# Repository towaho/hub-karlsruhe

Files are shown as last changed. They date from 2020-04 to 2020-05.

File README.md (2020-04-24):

# Herstellung der Gestelle - vom Druck bis zur Anlieferung
Vielen Dank, dass ihr uns mit dem Druck von Gestellen unterstützen wollt. Ihr findet hier alle wichtigen Informationen zum Ablauf im Hub Karlsruhe.
Alle weiteren Informationen zur Orga sowie ein FAQ findet ihr in unserem Doc [Organisation HUB Karlsruhe](https://docs.google.com/spreadsheets/d/1wsZU-VTYREOStcnClETrNQFkIYqHXFwlxU8IcKh8BXk)

Die Koordinierung für den Großraum Karlsruhe erfolg im Kanal [#hub-karlsruhe](https://app.slack.com/client/T010HM3B6BS/C010VSH5RD5). Dort helfen wir euch gerne bei Fragen und Problemen und ihr bekommt Infos zum aktuellen Stand.

In Karlsruhe wird aktuell ausschließlich das Modell Prusa rc3 bzw. die dazu lochkompatiblen Versionen V10 und V18 gedruckt.
Dieses Modell wird am meisten gewünscht und ist vor allem mit anderen Hubs kompatibel. Wir möchten euch daher bitten, nur dieses zu drucken und anzuliefern. Achtet bitte darauf, dass ihr **NICHT** aus versehen die slim Variante druckt. Die STL-Dateien sowie Hinweise zum Drucken findet ihr weiter unten.

Der Zusammenbau erfolgt in den beiden FabLabs. Ihr müsst also keine fertigen Schilde anliefern, sondern nur die gedruckten Gestelle und Stabis. Falls ihr passende Folien oder Loch-Gummiband beschaffen könnt, meldet euch aber gerne im slack Kanal bei uns oder direkt beim [Orga-Team](https://docs.google.com/spreadsheets/d/1wsZU-VTYREOStcnClETrNQFkIYqHXFwlxU8IcKh8BXk/edit#gid=139873882) per direct message.

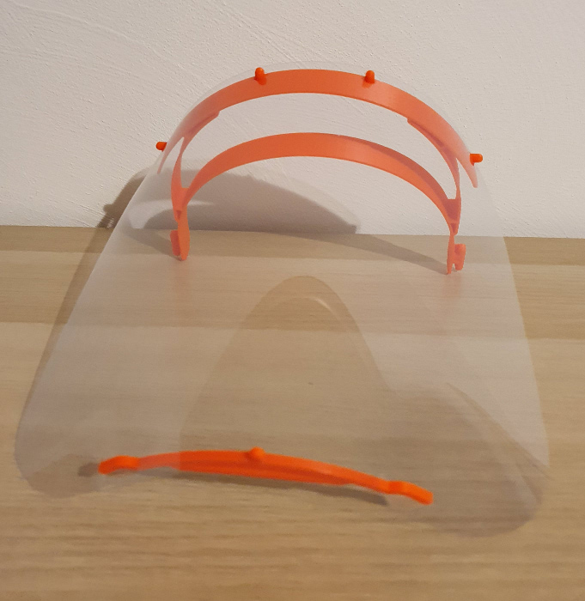
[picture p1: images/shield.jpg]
Faceshield


## Eintrag als Drucker
Tragt euch bitte im [doc in der Tabelle "Kapazitäten Gestelle"](https://docs.google.com/spreadsheets/d/1wsZU-VTYREOStcnClETrNQFkIYqHXFwlxU8IcKh8BXk/edit#gid=0) ein und gebt bitte eure Slack ID mit an. An eure Slack-ID kommt ihr wie folgt:
* In Slack in deinem Fenster oben Links auf das Feld "MakerVSVirus" klicken
* auf Profil Anzeigen / View Profile klicken
* Der Link wird dann im Browser in der URL-Leiste angezeigt

Die beiden geliefert Spalten sind schreibgeschützt und werden von den beiden Hubs verwaltet.

Spalte | Hinweise
------------ | -------------
Anzahl gedruckt | Hier bitte die Summe aller bereits gedruckten Gestelle eintragen (inklusive der bereits ans HUB gelieferten)
Anzahl in Arbeit | Hier könnt ihr eintragen, wie viele Gestelle ihr zur Zeit gleichzeitig im Druck habt. Wenn ihr gerade nicht drucken könnt, bitte auf 0 ändern.
mögliche Anzahl pro 24h | Tragt hier bitte nur ganze Zahlen ein und nicht "5-10" oder ähnliches.

## Material
PETG sowie PLA gehen. Bevorzugt wird PETG, da besser reinigbar. Die Farbe ist grundsätzlich egal. Sie sollte natürlich nicht ganz so peinlich sein. 

## STL Dateien
### Gestell
Unsere Empfehlung: [Covid-19 Shield v18.stl von Yannic Schröder](https://github.com/yschroeder/face-shield/raw/master/stl/Covid-19%20Shield%20v18.stl)

Wenn ihr Probleme mit der Haftung auf dem Druckbett habt, könnt ihr auch die [Version mit Lily Pads](https://github.com/yschroeder/face-shield/raw/master/stl/Covid-19%20Shield%20v18%20Lily.stl) nutzen. Das erhöht jedoch den Aufwand bei der Nachbearbeitung. Bei einem Drucker mit beheiztem Druckbett, richtig eingestellter Temperatur und korrekt justierter Z-Achse, solltet ihr aber auch ohne Pads keine Haftungsprobleme bekommen.

Für den Prusa i3 mit der Standard 0.4er nozzle findet ihr [hier eine fertige Projektdatei](https://github.com/towaho/hub-karlsruhe/raw/master/stl/Covid-19_Shield_v18_twin.3mf) mit zwei Oberteilen. Der [PrusaSlicer 2.2](https://www.prusa3d.de/prusaslicer/) unterstützt auch out of the box den Ender 3.

#### Alternativen (Bitte NICHT die slim Variante drucken)
* [Prusa rc3 ohne Text](https://media.prusaprinters.org/media/prints/25857/stls/270587_b59f75d0-4b8a-4999-8417-e5e75874ff98/covid19_headband_rc3.stl)
* [Covid-19 Shield v10](https://github.com/yschroeder/face-shield/raw/master/stl/Covid-19%20Shield%20v10.stl)

Es gibt zwar von Prusa auch eine Vorlage für kleinere Druckbette, diese müssen aber zusammen geklebt werden. Wir haben jedoch das Feedback erhalten, dass bei diesen der Tragekomfort nicht so gut ist. Daher diese Version bitte nicht mehr drucken.

### Stabi ("Unterteil")
Das Unterteil bitte nicht mehr drucken. Zur Zeit liefern wir alle Schilde ohne aus, da die Folie dick genug ist.

## Druck
Mit den Standardeinstellungen beträgt die Druckdauer eines Gestells in PETG ca. 2:30h. Die V18 ist von Yannic für den schnellen Druck optimiert worden. Bevor ihr diese nutzt, lest euch bitte vorher die [Doku von Yannic](https://github.com/yschroeder/face-shield) durch und stellt eueren Drucker entsprechend ein. Eine [deutsche Übersetzung](https://github.com/crix26/face-shield/blob/master/README.md) erstellt aktuell Christoph C. Mit Yannics Einstellungen könnt ihr ein Oberteil mit einem prusa i3 in PETG in ca. **0:43h** drucken. Zwei Gestelle gleichzeitig in 1:27h.

Beachtet bitte auch die Hinweise unter "Advanced Parameter Tuning" sowie Holes:

**Extrusion width / Extrusionsbreite**
* External perimeters / Außenkontouren: 1.00mm
* solid infill / Massives Infill: 0.55mm
* top solid infill / oberes massives Infill: 0.55mm

Hier zum Vergleich eine Detailaufnahme mit 0.87mm. Es sind an den T-Kreuzungen deutlich kleinere Löcher zu erkennen:
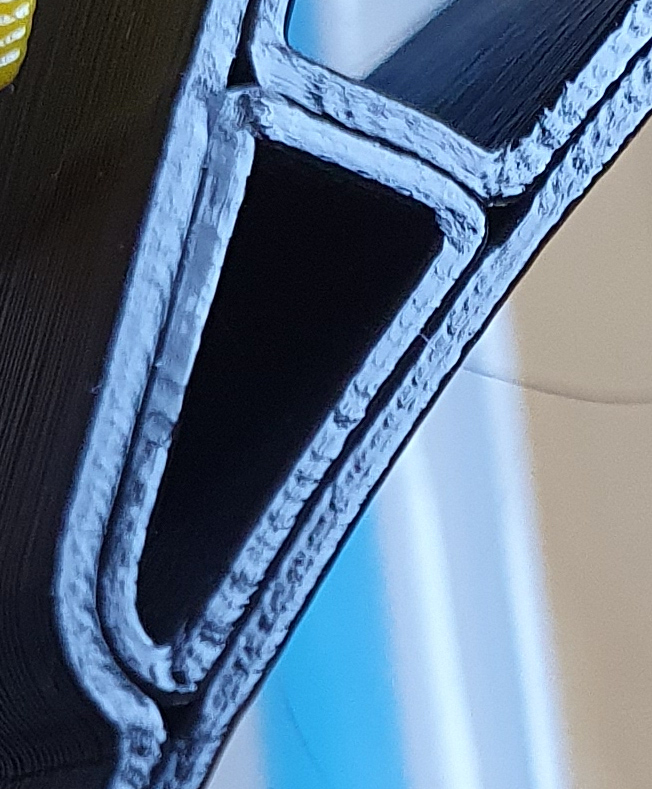
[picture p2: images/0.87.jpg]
0.87mm external perimeters


Mit 1.00mm sind zwar noch kleine Rillen vorhanden, aber die Löcher sind zu:
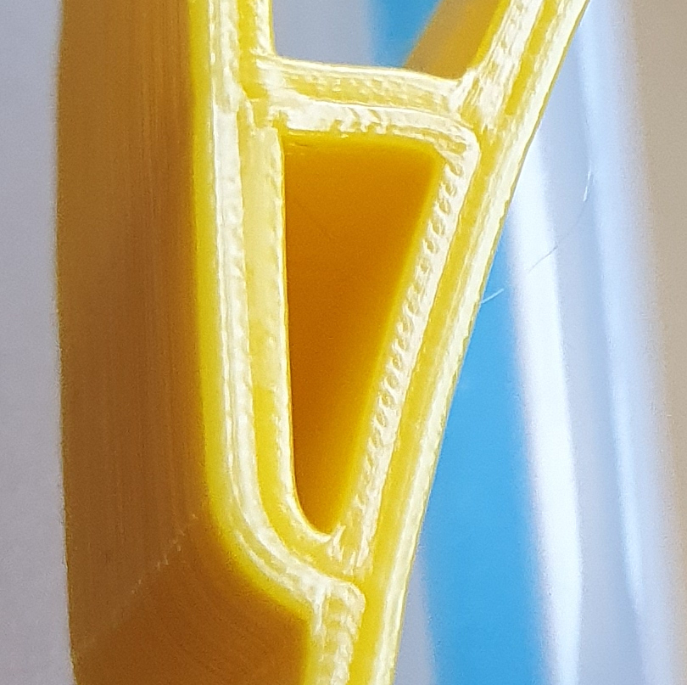
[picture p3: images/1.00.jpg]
1.00mm external perimeters


Alternativ könnt ihr auch wie von Yannic beschrieben den "Extrusion multiplier" erhöhen.

Wenn ihr die oben verlinkte Projektdatei nutzt, sind die hier beschriebenen Einstellungen schon alle mit drin. Um die angebenenen Druckzeiten zu erreichen, müsst ihr aber auch noch wie von Yannic beschrieben die Werte für "Max volumetric speed" unter "Filament Settings" -> Advanced -> "Print speed override" anpassen. Ein guter Startwert ist 8 mm³/s. Der i3 schafft mit 0.4er nozzle aber im Normalfall auch 17mm³/s. Am besten erhöht ihr wie von Yannic beschrieben den Wert in 2er Schritten, bis ihr einen optimalen Wert für euren Drucker gefunden habt.

### Hinweise

Das Drucken der Gestelle ist kein Wettbewerb wer am meisten druckt. Wenn ihr nicht die von Yannic empfohlenen Einstellungen nutzt, dann am besten mit 3 Perimeter (Wände) drucken. Vor dem ersten Druck sollte auch in der Vorschau überprüft werden, ob keine Lücken entstehen.

Aktuell raten wir davon ab, die Gestelle übereinander als Stacks zu drucken. Die bisherigen Erfahrungen haben gezeigt, dass gut 80% der Stacks nicht verwendbar sind (kleben zu stark aneinander, Boden schlecht verklebt, Probleme beim Desinfizieren).

### Empfehlungen für das BASF PET Fillament
Beachtet bitte, dass es sich hierbei um PET und nicht um PETG handelt. Der Schmelzpunkt ist niedriger und somit auch die Drucktemperatur. Wenn ihr ein PEI beschichtes Druckbett nutzt, dann solltet ihr beim ersten Druck die z-Achse 0.1mm höher (weiter Weg vom Druckbett) einstellen und euch in 0.01er Schritten an 0 annähern. ZU NAH AM BETT = RISIKO dass die Beschichtung beim Ablösen am Druckteil statt am Druckbett klebt! Löst die Teile am besten, bevor das Druckbett vollständig abgekühlt ist. 

Als Ausgangswerte für eigene Tests eignen sich:
* Druckbett 75°C (wenn die Haftung zu stark ist, senkt die Temperatur ein wenig)
* Nozzle: 220°C 
* Lüfter: 100%, durchgängig an, bis auf die ersten 1-2 Schichten
* Geschwindigkeit: max 60mm/s
* retraction Speed: 45mm/s vermindert das stringing nochmal ein wenig. Wenn ihr unsicher seid, lasst die default Einstellungen

Ein wenig stringing hatten wir auch mit diesen Einstellungen noch. Meldet euch gerne im channel, wenn ihr Probleme oder bessere Einstellungen gefunden habt.

Wer cura nutzt, findet hier auf der [Herstellerseite](https://www.ultrafusefff.com/3dprintingprofiles/) Profile für das Filament. Diese haben wir aber aktuell noch nicht getestet.

## Qualitätskontrolle
**Die hier beschriebenen Tests gelten nur für die V18**. Die anderen Modelle sind nicht so flexibel und könnten brechen obwohl sie für den Bau der Schilde nutzbar sind.

Viel wichtiger als die Druckzeit ist, dass die Qualität am Schluss stimmt. Prüft bitte insbesondere beim Druck der V18 mit nur zwei Perimeter, ob diese sauber miteinander kleben. 

So sollte es **nicht** aussehen (Delamination)
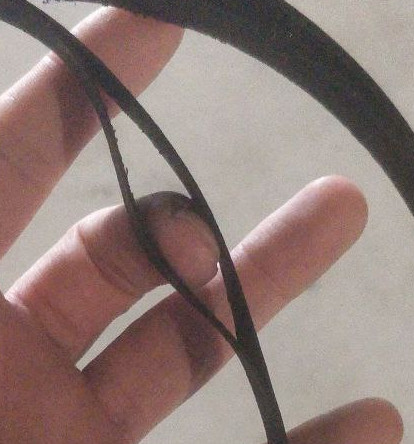
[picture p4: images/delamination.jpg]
Delamination


Führt am besten nach eurem ersten Druck den [hier beschriebenen Test](https://github.com/yschroeder/face-shield/blob/master/quality_control.md) durch. Meldet euch bitte im #hub-karlsruhe wenn ihr Qualitätsprobleme habt. **Vor der Abgabe/Abholung bitte alle Teile entsprechend prüfen.**

## Abgabe/Abholung
Abgeben könnt die fertig gedruckten Teile in einem der beiden FabLabs:

**FabLab Karlsruhe e.V.**
```
Alter Schlachthof 13a (gegenüber Substage / Alte Hackerei)
76131 Karlsruhe
Tel.:  +49 721 60906012	
```

**FabLab Bruchsal e.V. i.G.**
```
Werner-von-Siemens-Straße 2-6
Gebäude 5137c
76646 Bruchsal
Tel.: +49 151 25351131
```

Im Google Docs gibt es eine Ampel, ob das Lab besetzt ist. Fragt bitte vorher zur Sicherheit noch einmal telefonisch nach, damit ihr euch nicht umsonst auf den Weg macht.

Für alle die keine Möglichkeit haben, die Teile in Karlsruhe oder Bruchsal abzugeben, gibt auch ca. 2 mal die Woche eine Abholtour, bei der ihr eure Teile kontaktlos abholen lassen könnt. 

Damit wir euch bei Problemen direkt ansprechen können, bitte die Gestelle in einem Müllbeutel verpacken und einen Zettel mit folgenden Infos dazu legen:
* Name
* Slack ID
* Material
* Druckdatum/Zeitraum

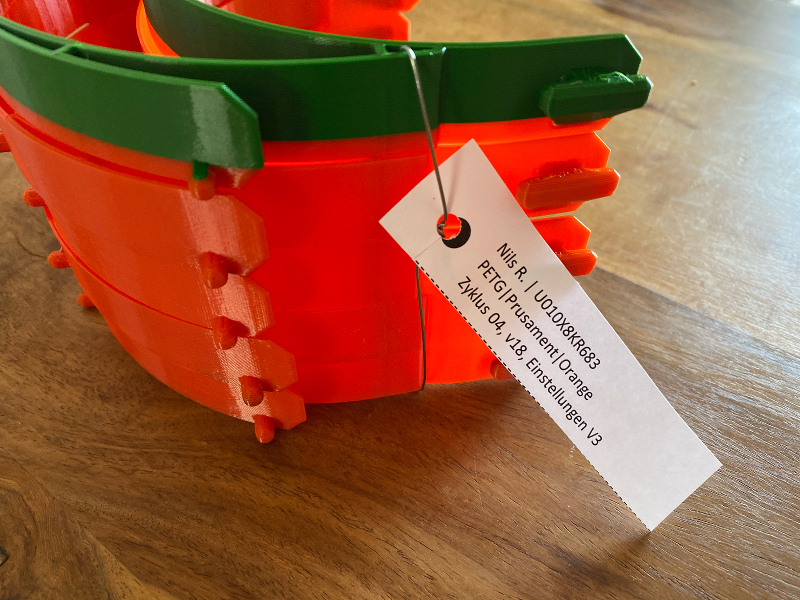
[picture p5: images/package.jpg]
Fertig zur Abgabe


Das Desinfizieren der Teile ist nicht notwendig. Die Empfänger werden die Schilde sowieso desinfizieren und Desinfektionsmittel ist zur Zeit ebenfalls knapp.

Falls wir die gelieferten Teile nicht im Sheet eingetragen haben, meldet euch bitte noch einmal bei uns.

[shield]: images/shield.jpg "Faceshield"
[1mmperimeters]: images/1.00.jpg "1.00mm external perimeters"
[0.87mmperimeters]: images/0.87.jpg "0.87mm external perimeters"
[delamination]: images/delamination.jpg "Delamination"
[package]: images/package.jpg "Fertig zur Abgabe"

## **Auslieferung**

Vielen Dank, dass du dich bereit erklärt hast auch fertig verpackte Gestelle auszuliefern.

Im folgenden sind einige Dinge beschrieben, die es zu beachten gibt, sowie FAQ.

### Auftragsbearbeitung/Zugriff auf die Tabelle

Die Auftragsbearbeitung wird über ein extra Google Sheet organisiert. Dies hat den Grund, dass die Kundendaten nicht für alle öffentlich einsehbar sein sollen. Kommt ein Auftrag über das Formular auf der Website rein, landet dies automatisch im Reiter "Kunden Daten". In den Reitern "[Labstandort]-Schilde offen" und "[Labstandort]-Masken offen] seht ihr welche Aufträge noch offen sind und entsprechend bearbeitet werden müssen/sollen.

Wichtig ist der Status der Bestellung. Steht dieser auf "In Herstellung" kann man sich den Auftrag zur Auslieferung reservieren. Mehr dazu in Ablauf Auslieferung.

Zugriff auf die Tabelle erhaltet ihr von einem der Admins. Das sind derzeit Robert & Nils R. .

Vor allem Robert schreibt des Öfteren Nachrichten zum Koordinieren, welche Lieferungen für den jeweiligen Tag anstehen. Diese sollten priorisiert abgearbeitet werden.

### Ablauf Auslieferung

1. Zugriff auf die Tabelle (siehe oben)
2. Auftrag von Robert (oder Nils) annehmen oder initiativ Auftrag annehmen (eher zu empfehlen wenn man schon einige Aufträge ausgeliefert hat und die Abläufe und Priorisierungen kennt)
3. In die Tabelle bei "Auslieferung durch" eintragen [Wichtig: Immer im Reiter "Kundendaten" Eintragungen vornehmen]
4. Klären, wann du die Lieferung im Lab abholen kannst. Im Reiter Kundendaten steht in der Spalte "sammeln in" wo du die Lieferung holen kannst.
5. Beim Kunden anrufen und Bescheid geben, dass und wann du vorhast auszuliefern. Eventuell Termin ausmachen, wenn nicht am selben Tag möglich.
6. Status von "In Herstellung" auf "In Auslieferung" ändern
7. Ausliefern (dabei erwähnen, dass wir uns immer über Bilder der Masken "Im Einsatz" zur Veröffentlichung auf unserer Website freuen) 
8. Status von "In Auslieferung" auf "Erledigt" ändern, Datum bei "Erledigt am" eintragen, Summe bei "[Art der Lieferung]-Erledigt-[Labstandort]" eintragen

Herzlichen Glückwunsch. Du hast erfolgreich deine erste Auslieferung durchgeführt! 

### FAQ oder was du noch wissen solltest: [bzgl. Auslieferung]

**Wie gehe ich mit Spenden um?**

Am Besten ist es, du verweist den Kunden auf das Spendenformular auf der Website. In der Regel stehen die Informationen dazu auch auf dem Zettel, welcher der Verpackung beigelegt ist.

Manche Einrichtungen oder Arztpraxen drücken einem auch manchmal einfach einen Umschlag in die Hand. Dieser sollte dann im Lab abgegeben werden. [Wichtig. Wenn der Kunde eine Spendenquittung wünscht, muss die Spende über das Spendenformular stattfinden!]

**Was soll ich sagen, wenn nach dem Preis gefragt wird?**

Grundsätzlich lautet die Antwort, dass die Schilde von uns kostenlos geliefert werden. Allerdings ist es schlau, immer darauf zu verweisen, dass wir ein Spendenformular haben und uns immer über Spenden freuen, da das Ganze nur so finanziert wird. [Wichtig: Die Spende ist freiwillig und so muss das auch kommuniziert werden. Es gibt auch Einrichtungen, denen schlichtweg das Geld fehlt und genau dafür gibt es uns ja]

**Was soll ich am Telefon sagen?**

Da gibt es kein Universalrezept. Ich [Michael Ewig] sage immer, dass ich von MakerVsVirus/CoronaHilfe Karlsruhe bin, es um die Gesichtsmasken geht, die bei uns bestellt wurden und dass ich diese gerne zu Zeitpunkt XY ausliefern will (und ob das möglich ist). Oder eine Variation davon.

**Ich habe noch Fragen und weiß nicht an wen ich mich melden soll.**

Generell ist Nils R. (Auftragsbearbeitung) immer eine gute Anlaufstelle für alle Themen der Auftragsbearbeitung und Auslieferung. Antworten können auch Robert [FabLab KA] oder Michael Ewig [Hub Karlsruhe] liefern.

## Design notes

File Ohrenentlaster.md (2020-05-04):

# Herstellung Ohrenentlastung
Hier findet ihr alle wichtigen Informationen zum Druck der Ohrenentlaster. Es gibt im Netz sehr viele Versionen und Varianten. Wir haben uns in Karlsruhe für die light Version von Yannic entschieden. Wir drucken bis auf weiteres erst einmal nur die Lang-Version.

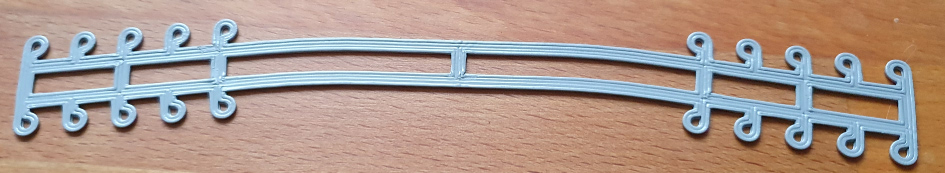
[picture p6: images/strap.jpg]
Ohrenentlastung


## Material
Bitte nur PET,PETG oder ABS verwenden. Wenn ihr nur PLA drucken könnt, dann bitte vorab mit uns abklären. Farbe ist auch hier grundsätzlich egal. Häufig gewünscht werden helle Farben (weiß, gelb, grün). Grundsätzlich könnt ihr alle Farben drucken, die eurer Meinung nach Ärzte und Pfleger gerne tragen.

## STL Dateien
### Gestell
Long Version [Surgical_Mask_Strap_light_long_v5.stl von Yannic Schröder](https://github.com/towaho/hub-karlsruhe/raw/master/stl/Surgical_Mask_Strap_light_long_v5.stl)

Für den Prusa i3 mit der Standard 0.4er nozzle findet ihr [hier eine fertige Projektdatei](https://github.com/towaho/hub-karlsruhe/raw/master/stl/surgical-mask-strap-light_long-table-v5.3mf) mit 7 Stück auf einem Druckbett.

## Druck
Mit den Einstellungen aus der Projektdatei könnt ihr 7 Stück in ca. 24 (PETG) - 30 (PET) Minuten drucken. Für den Prusa i3 mk3 haben wir eine fertige Projektdatei. Für andere Drucker findet ihr [hier die Hinweise von Yannic](https://www.prusaprinters.org/prints/30406-surgical-mask-strap-light). **HINWEIS:** In dieser Projektdatei ist die Standardversion enthalten. Wir drucken aktuell die Long Version 5. 

Wenn ihr [unsere Projektdatei](https://github.com/towaho/hub-karlsruhe/raw/master/stl/surgical-mask-strap-light_long-table-v5.3mf) nutzt, sind die von Yannic beschriebenen Einstellungen schon alle mit drin. Um die angebenenen Druckzeiten zu erreichen, müsst ihr aber auch noch wie von Yannic beschrieben die Werte für "Max volumetric speed" unter "Filament Settings" -> Advanced -> "Print speed override" anpassen. Das BASF PET kann man beim Prusa i3 mk3 auf ca. 10-12 mm³/s setzen. PETG könnt ihr mit 15-17 mm³/s drucken. Wenn ihr Lücken im Druck habt, dann müsst ihr den Wert verringern. 

### Empfehlungen für das BASF PET Fillament
Beachtet bitte, dass es sich hierbei um PET und nicht um PETG handelt. Der Schmelzpunkt ist niedriger und somit auch die Drucktemperatur. Wenn ihr ein PEI beschichtetes Druckbett nutzt, dann solltet ihr beim ersten Druck die z-Achse 0.1mm höher (weiter Weg vom Druckbett) einstellen und euch in 0.01er Schritten an 0 annähern. ZU NAH AM BETT = RISIKO dass die Beschichtung beim Ablösen am Druckteil statt am Druckbett klebt! Löst die Teile am besten, bevor das Druckbett vollständig abgekühlt ist (sie müssen aber kurz abkühlen, damit sie sich beim Ablösen nicht verziehen). Im Gegensatz zu den Gestellen, haften diese Teile aufgrund der größeren Fläche deutlich besser. Ihr könnt somit in den meisten Fällen die Temperatur des Druckbetts reduzieren. 

Als Ausgangswerte für eigene Tests eignen sich:
* Druckbett ca. 60°C (wenn die Haftung zu stark ist, senkt die Temperatur ein wenig; Prusa i3 mk3 druckt mit powded bed bei 55°C wunderbar)
* Nozzle: 230°C 
* Lüfter: min 30%, max 50%, durchgängig an, bis auf die ersten 3 Schichten
* Geschwindigkeit: max 200mm/s (wird durch Max volumetric speed reduziert)

## Qualitätskontrolle
Viel wichtiger als die Druckzeit ist, dass die Qualität stimmt. Reduziert im Zweifelsfall lieber die Geschwindigkeit. Ausschus bitte separat sammeln und als Ausschuss im FabLab abgeben. 

Hier seht ihr, wie die fertigen Teile aussehen sollen:
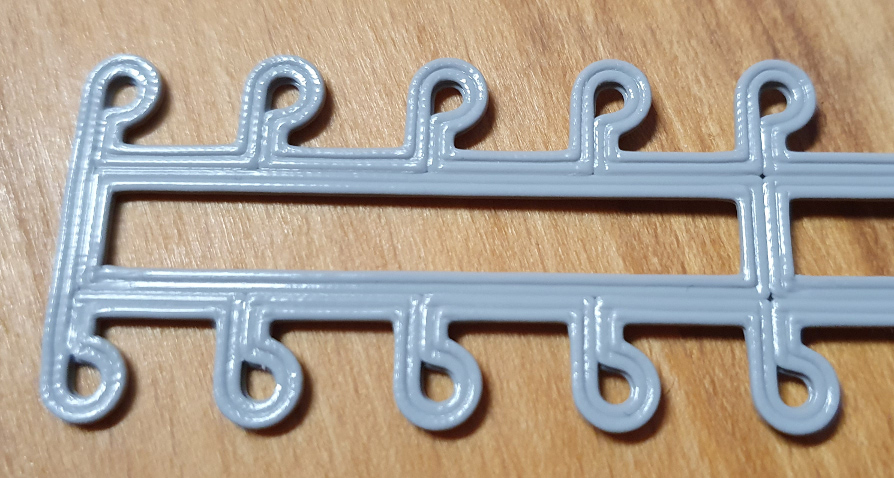
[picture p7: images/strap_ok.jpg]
So sollten die Teile aussehen


Prüft bitte, bei jeder Charge, ob sich die Teile gut biegen lassen:
Qualitätstest1
Qualitätstest2 
Qualitätstest3 

Hier seht ihr ein paar typische Probleme und Hinweise, was zu tun ist:

**Druck mit Infill**
Wenn eure Ösen keine Löcher haben, habt ihr mit Infill gedruckt. Das erhöht die Druckzeit und ist meist nicht verwendbar. Hier verfangen sich leicht die Haare:
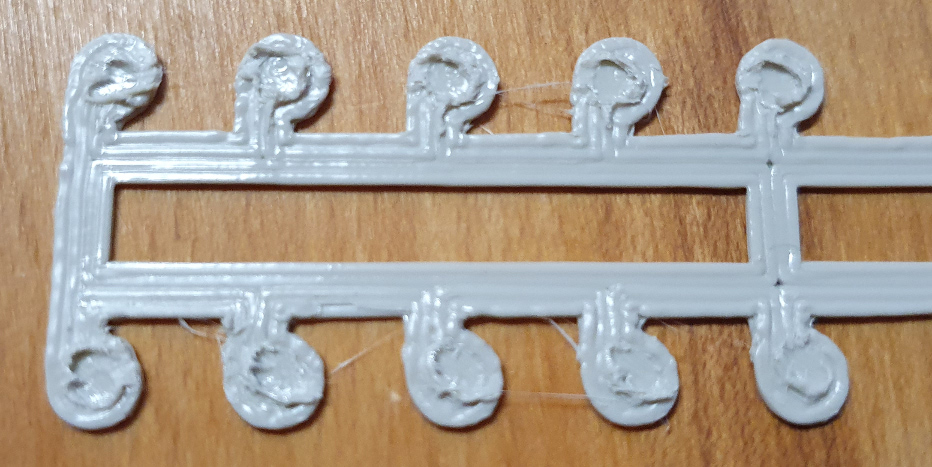
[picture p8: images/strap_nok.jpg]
mit Infill gedruckt


**Volumenstrom zu hoch**
Wenn ihr solche Unterbrechungen im Druck habt, schafft der Drucker den Volumenstrom nicht. Ihr müsst "Max volumetric speed" reduzieren.
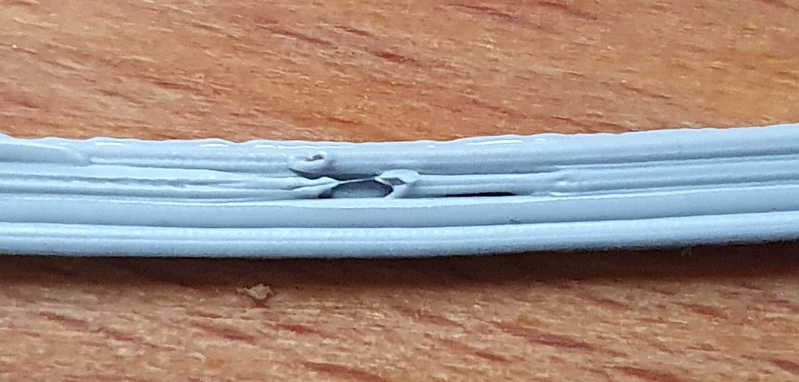
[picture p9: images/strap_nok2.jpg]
zu hoher Volumenstrom


Wenn ihr Probleme mit dem Druck habt, meldet euch bitte im channel und schickt bitte ein Foto des Drucks mit.

**Wenn ihr auch mit Unterstützung und Nachjustierung die hier beschriebene Qualität mit eurem Drucker nicht erreichen könnt, dann macht es leider wenig Sinn, die Teile weiter zu drucken.**

**Entfernt bitte stringing (auch dünne Fäden) vor der Abgabe** 

## Abgabe/Abholung
**Bündelt bitte immer 10 Teile mit Kabelbinder oder Draht und packt sie am besten in einen Gefriebeutel. Bitte nicht lose abgeben.**
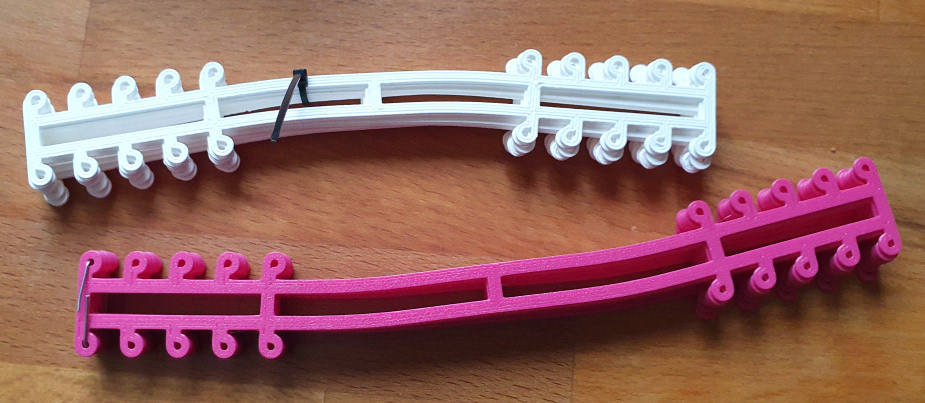
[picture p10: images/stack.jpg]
Bündel


Wir haben in der Orga Tabelle einen Tab für die Ohrenentlastung angelegt. Tragt eure Drucke bitte dort genau so ein, wie bisher bei den Gestellen. Abgeben könnt die fertig gedruckten Teile in einem der beiden FabLabs:

**FabLab Karlsruhe e.V.**
```
Alter Schlachthof 13a (gegenüber Substage / Alte Hackerei)
76131 Karlsruhe
Tel.:  +49 721 60906012	
```

**FabLab Bruchsal e.V. i.G.**
```
Werner-von-Siemens-Straße 2-6
Gebäude 5137c
76646 Bruchsal
Tel.: +49 151 25351131
```

Im Google Docs gibt es eine Ampel, ob das Lab besetzt ist. Fragt bitte vorher zur Sicherheit noch einmal telefonisch nach, damit ihr euch nicht umsonst auf den Weg macht.

Damit wir euch bei Problemen direkt ansprechen können, bitte folgenden Infos dazu legen:
* Name
* Slack ID
* Material
* Druckdatum/Zeitraum

Falls wir die gelieferten Teile nicht im Sheet eingetragen haben, meldet euch bitte noch einmal bei uns.

[strap]: images/strap.jpg "Ohrenentlastung"
[strap_ok]: images/strap_ok.jpg "Ohrenentlastung ok"
[strap_nok]: images/strap_nok.jpg "Ohrenentlastung Infill"
[strap_nok2]: images/strap_nok2.jpg "Ohrenentlastung Volumenstrom"
[stack]: images/stack.jpg "Bündel"
[quali1]: https://media.prusaprinters.org/thumbs/cover/640x480/media/prints/30406/images/302146_9f2713b5-90f6-4e76-930d-09c3edcbd2a6/img_7446.jpg "Qualitätstest1"
[quali2]: https://media.prusaprinters.org/thumbs/cover/640x480/media/prints/30406/images/302147_2a2984e1-f2fe-46d2-af92-ccdb00599e71/img_7440.jpg "Qualitätstest2"
[quali2]: https://media.prusaprinters.org/thumbs/cover/640x480/media/prints/30406/images/302148_9b7cb500-3687-43e3-9823-841517991fbf/img_7447.jpg "Qualitätstest3"

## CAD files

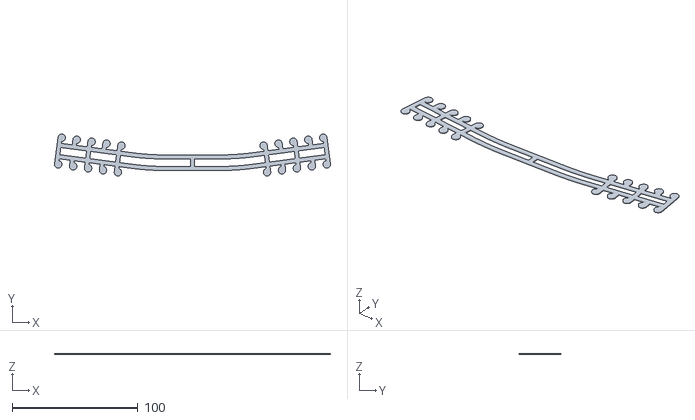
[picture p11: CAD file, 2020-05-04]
stl/Surgical_Mask_Strap_light_long_v5.stl
219.9 x 33.4 x 1.00

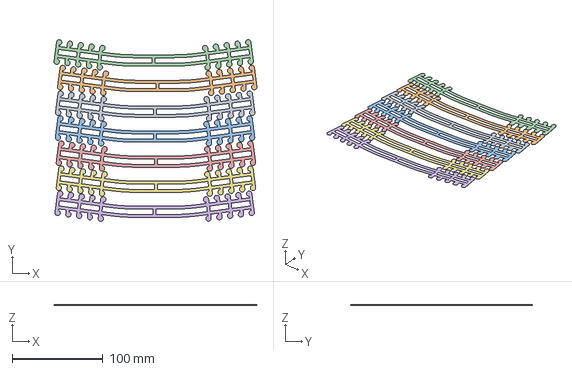
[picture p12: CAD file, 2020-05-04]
stl/surgical-mask-strap-light_long-table-v5.3mf
223.8 x 200.2 x 1.00 mm

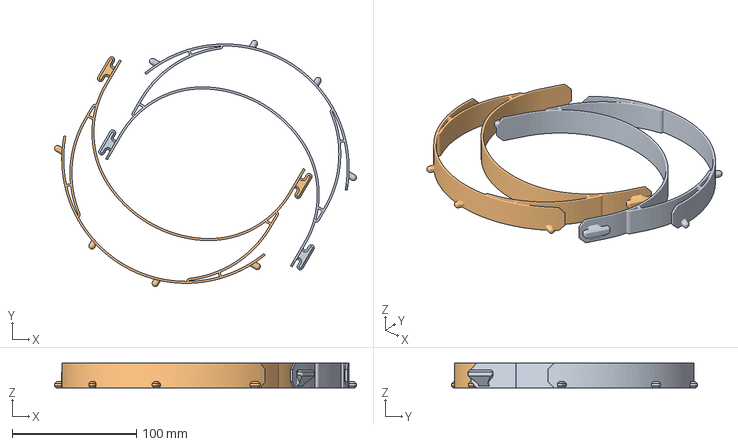
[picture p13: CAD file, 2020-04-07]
stl/Covid-19_Shield_v18_twin.3mf
242.7 x 197.8 x 20.0 mm

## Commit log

2020-04-06 added prusa slicer project file
    [Covid-19_Shield_v18_twin.3mf]
2020-04-06 added Yannics comments
    [Covid-19_Shield_v18_twin.3mf]
2020-04-06 added second shield
    [Covid-19_Shield_v18_twin.3mf]
2020-04-07 set Solid layers to 5
    [Covid-19_Shield_v18_twin.3mf]
2020-05-03 added long version with 5 eyes from yannic
    [Surgical_Mask_Strap_light_long_v4.stl]
2020-05-03 added surgical strap project file for prusa i3 mk3 with basf filament
    [surgical-mask-strap-light_long-table-v4.3mf]
2020-05-04 changed temperature
    [surgical-mask-strap-light_long-table-v4.3mf]
2020-05-04 replaced long version with v5 from yannic
    [Surgical_Mask_Strap_light_long_v4.stl, Surgical_Mask_Strap_light_long_v5.stl, surgical-mask-strap-light_long-table-v4.3mf, surgical-mask-strap-light_long-table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]
2020-05-04 updates print time infos
